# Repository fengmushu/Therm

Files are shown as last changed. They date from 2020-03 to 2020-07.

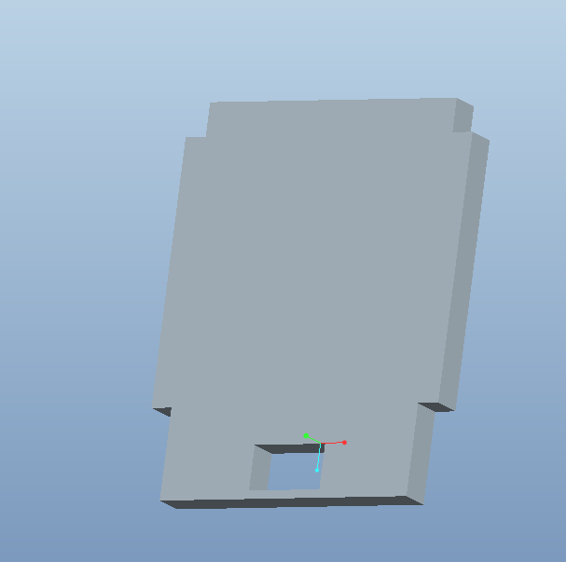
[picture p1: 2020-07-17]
doc/wm-smallgun/导光板设计资料/示意图.png

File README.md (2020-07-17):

[ROM]
- PB8-i2c-CLK
- PB9-i2c-DAT
- 可能是用于保存传感器NTC查表的
- 合法数据才会有i2c访问记录

[SPK]
- PD7-蜂鸣器

[LCD]
- LCD[1-4] - COM0/1/2/3 - PA9/10/11/12
- LCD[5-15] - S19/18/17/16/15/14/13/12/11/10/9 - PA4/5/6/7 - PC4/5 - PB0/1/2/10/11
- LCD[16-24] - S8/7/6/5/4/3/2/1/0 - PB12/13/14/15 - PC6/7/8/9 - PA8

[P1-DEBUG]
- SW-CLK
- SW-DIO
- VCC
- GND
- RSTB

[KEY]
- KEY[1:Trigger - 5] - PD6 - PC10/11/12 - PD2

[Anlog]
- PA15 - AV+ 3V
       - AV- -> GND
- PA0 -> 1-1.2v ViR
- PA1 -> NTC+800mV
- PA2 -> NTC-2000mV

- VIN+ 960mV
- VIN- 1000mV
- Yellow-NTC--2.0V
- Green-VIN--1000mV
- Black-NTC+-800mV
- Red-VIN+-960mV

[LED]
- LED-Light - PC13

Vra = Vcc - VntcL

- ('Vi(Tt)', array([-2.420154e+06,  5.435100e+04,  4.950000e+02]))
- ('Vi(Te)', array([ 1.589544e+06, -5.435100e+04, -4.950000e+02]))
- ('Ra(Te)', array([ 2.84148615e+05, -9.89025670e+03,  1.02357699e+02]))

- ViTt = At + Bt * Tt + Ct * Tt^2;
- ViTe = Ae + Be * te + Ce * te^2;

- 29-/+0.5 步长0.1
- fAPM, fCaBase, fHumFix;

#### MUST READ !!!
1. 标定部分, 需要预留Flash最后2个Block
2. 

原理:  
1. 传感器里面有两个单元: 光敏电池(辐射热堆) 和 温敏电阻(测环境温度); 
2. 光敏电池的电压 Vir 与 辐射源的温度 Tt 存在一张离散数据表 Vir-Tt;
3. 温敏电阻阻值 Ra 与 环境温度 Te 存在一张离散的数据表 Ra-Te;
4. 校准先后分为两步:
1. 标准温度下, 标定黑体
              * 操作: 黑体和环境都是35°和42°的稳定环境下, 测出对应的标定温度: 如 35.3, 41.8 分别保存到设备里面H,L
       2. 恒定黑体下, 标定环温
              * 操作: 改变环境温度, 测出相对于固定黑体温度的值, 计算NTC-变温校准系数

#### 历史数据存储
1. 物体模式和人体模式, 各自分别保存32组数据;
2. 显示时: 根据当前所选模式, 各自读取 1) 保存的历史数据, 直接显示;
3. 历史数据存储位置为: I2C ROM的前半部分;
4. 历史数据存取方式,用环形栈结构;
5. 物/人切换后, 历史数据下标复位到栈顶;

#### 校准数据保存
1. Flash 的 0xFC00 块存放产测和校准数据(最大块容量 512Byte);
2. I2C ROM 除了保存历史数据之外, 最后64Byte也保存一份校准数据;
3. Flash的校准数据与I2C的, 写入时保持同步;
4. Flash的校准数据与I2C的, 加载时只判断有无;
5. Flash的校准数据和I2C有差异时: 以I2C保存的为准(处理传感器差异, 不需要升级软件, 修改I2C即可);
6. 校准数据需要MagicNumber区别, 防止软件版本变更数据结构;

7. 校准数据里面需要包含传感器的拟合参数 --- 有待商榷;

Rx * 100K / (Rx+100K) * I + 100K * I = 2.5

Vx = Rx * 100K / (Rx + 100K) * I

I = (2.5 - Vx) / 100K

Vx = Rx * ( 2.5 - Vx) / ( Rx + 100K )

Vx * Rx + Vx * 100K = (2.5 - Vx) * Rx

Vx * 100K = (2.5 - 2 * Vx) * Rx

Rx = Vx * 100K /  (2.5 - 2 * Vx)

1. R45 2k
2. R41,R43,R46 1k
3. R44 680k

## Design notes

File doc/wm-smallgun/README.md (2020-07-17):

1. 第一排3颗按键,柄过长, 会导致装配之后按不下去, 或者螺丝打紧之后, 按不下去;
2. 电池仓, 尾部弹片会掉出去;
3. 屏幕底部 外框厚度差0.2mm, 导致屏幕装配不可靠;

4. 屏幕导电PIN脚间距: 0.5625mm, 屏幕和外壳框之间的缝隙 就有 0.68mm
5. RC复位电路设计优化

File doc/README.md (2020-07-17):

### 2020-05-05

1. 校准时, 允许一个点 37/42, 采样失败时, 继续重新采样;
2. 校准时, 至少采样3次, 间隔一个打印周期(50ms-100ms), 计算多次采样值, 方差为零才算有效值, 否则继续采样;
3. 超过 10 次都是无效值(说明手抖), 蜂鸣器长鸣告警, 重新进入校准;
4.

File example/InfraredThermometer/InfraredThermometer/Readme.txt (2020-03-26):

================================================================================
                                样例使用说明
================================================================================
版本历史 
日期        版本    负责人         IAR     MDK         描述
2020-03-12  SE2.0     Lux          xxx     5.26       first version
================================================================================
功能描述
================================================================================
本额温枪样例为开发过程版本，旨在提供基本功能模块单元的操作及架构，为应用开发者提供快速原型构建，
将更多的精力用在业务开发上及系统调试上。

================================================================================
测试环境
================================================================================
辅助工具:
---------------------

配套硬件参考:
---------------------
“Hm-Meter-源文件.rar”及“Hm-Meter-PDF BOM.rar”
硬件参考资料可向销售窗口获取

================================================================================
操作步骤
================================================================================
1) 程序编译后下载到配套方案板；
2) 复位或初次上电LCD全显闪烁两次，保持全显；
3) 参考软件流程（操作）进行验证；

================================================================================
功能说明
================================================================================
1）打开工程编译并运行。
2）可根据不同的具体硬件IO功能修改"board_stkhc32l13x.h"板级接口文件，或自行定义功能。
3）数据采集部分使用内部ADC连续16次采样取均值的方式采样外部经过OPA调理过的信号。
4) 显示部分提供了配套原理图“Hm-Meter-源文件.rar”及“Hm-Meter-PDF BOM.rar” 所使用LCD的数据结构及操作，同时包括HC32L13X_STK的LCD参考。
5) 数据处理算法参考“nna.h"及样例。
6) 按键及其他基础功能模块较为简单，通常为基本的IO操作，本应用提供了基本的初始化操作。

================================================================================
注意
================================================================================
-->>本样例实现了额温枪方案的基本方法及架构，基于华大MCU HC32L136进行构建，算法已基于现有硬件配套传感器进行验证；
-->>仅可为应用开发者提供快速原型参考，具体的端口、业务功能、数据处理应以实际采纳的硬件为准，进行程序修改及调试；
-->>如果硬件发生更改，请对应修改软件及配置;
-->>如果传感器发生更改，请更新“inf_config”中的V-T表及NTC表;
-->>LCD使用如有不同，需要根据手册修改编码及端口配置;
-->>本应用示例对于硬件及软件逻辑功能不做任何限制，主要用于参考原型，便于对进行自己产品的差异化开发;
================================================================================

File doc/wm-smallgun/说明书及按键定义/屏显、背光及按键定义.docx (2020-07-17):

# 屏显及按键

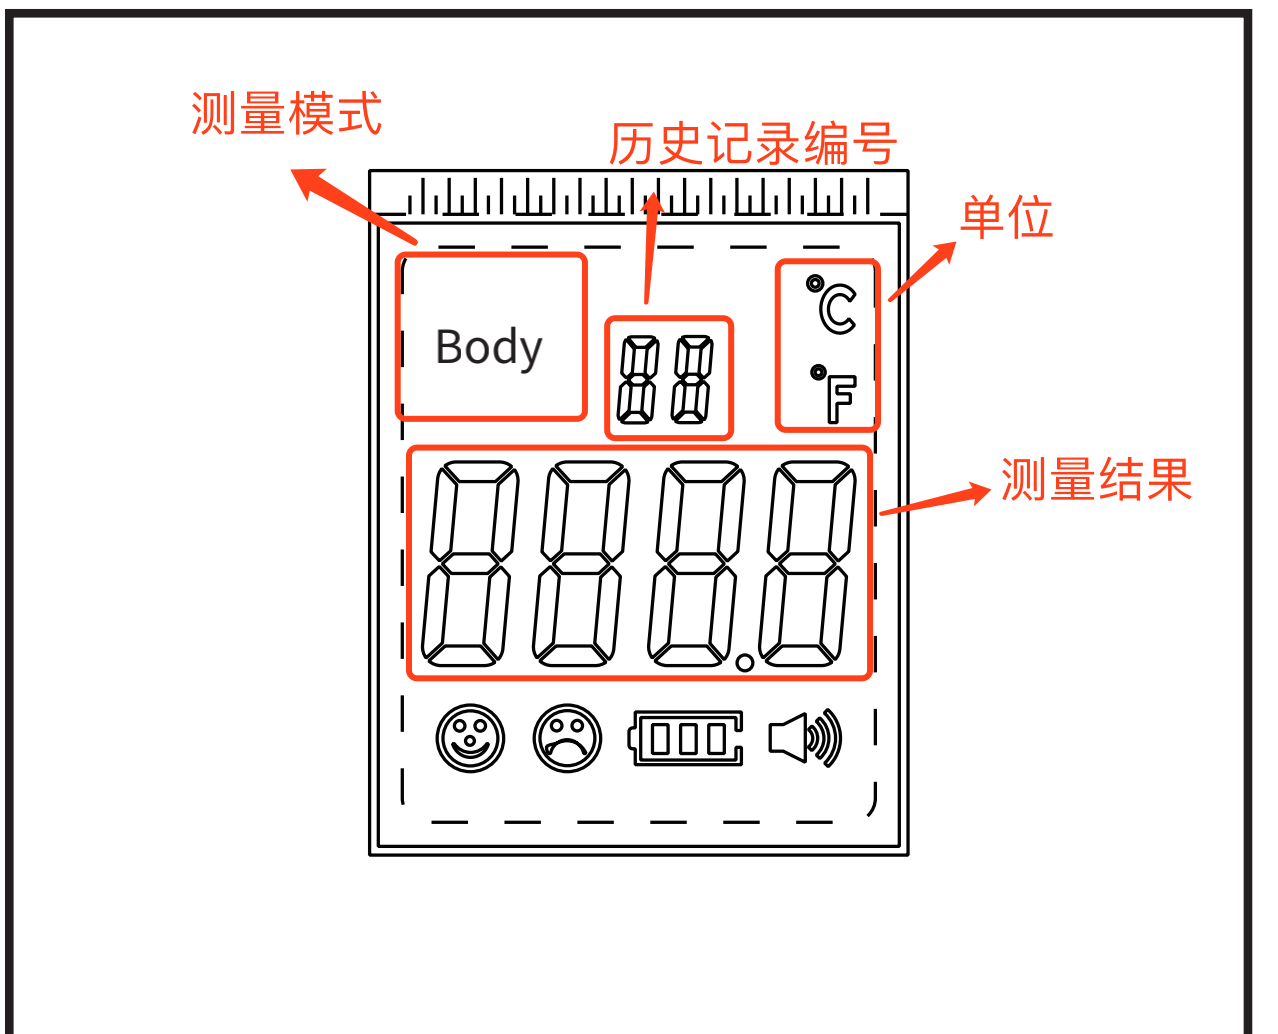
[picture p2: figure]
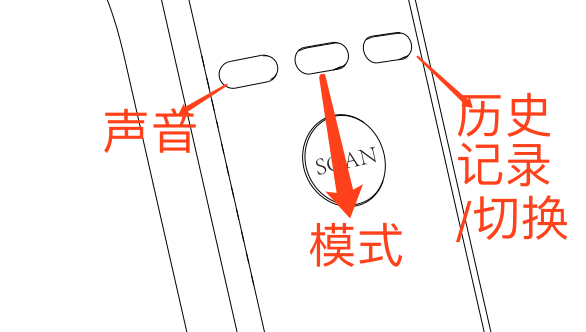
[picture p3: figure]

# 按键

## 声音

直接开启或关闭声音，影响屏幕上面的是否显示。

## 模式

两种设置

A：测试模式：物温模式或体温模式

B：单位模式：F or C

可以多次按此键进行设置切换

在A, B任一设置模式下，通过右侧切换键进行设置。

## 历史记录/切换

A. 在设置模式下，切换设置
B. 在扫描模式下进行，查看历史记录。

## 笑脸及背光

体温模式下：

=0 背光黄色，显示Lo，哭脸

< =37.2 背光绿色，笑脸

<=38 背光黄色，哭脸

其他 背光红色，哭脸

=100 背光红色，显示Hi，哭脸

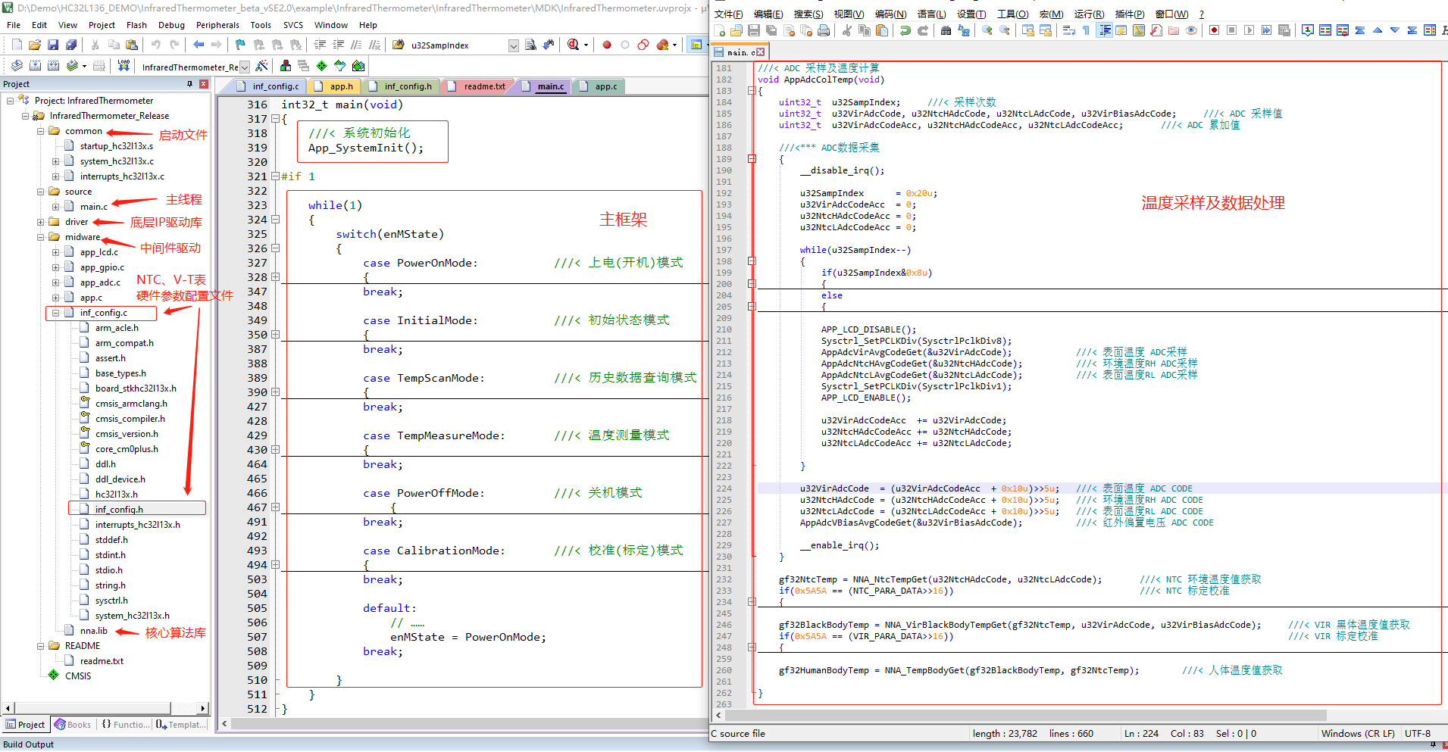
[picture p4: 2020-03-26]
工程及软件简介.png

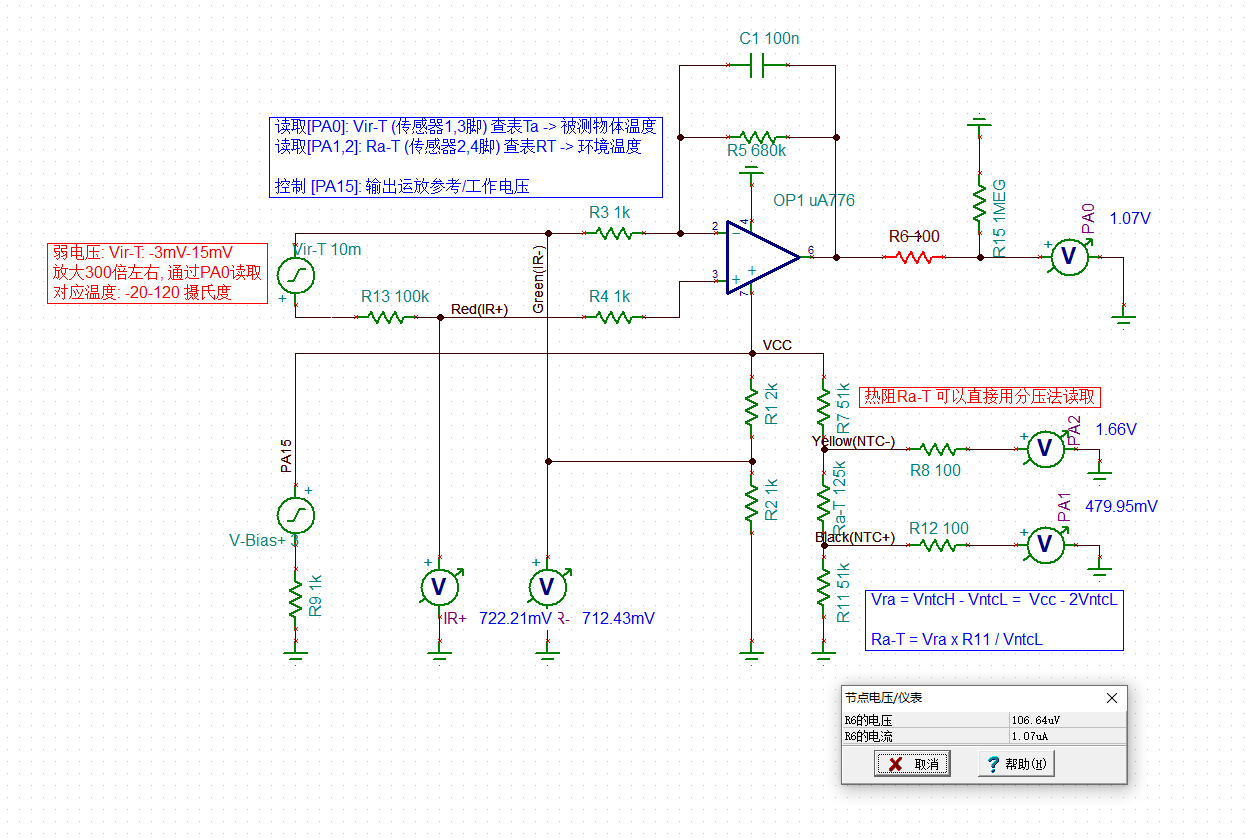
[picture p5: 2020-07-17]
TINA-SIM.png

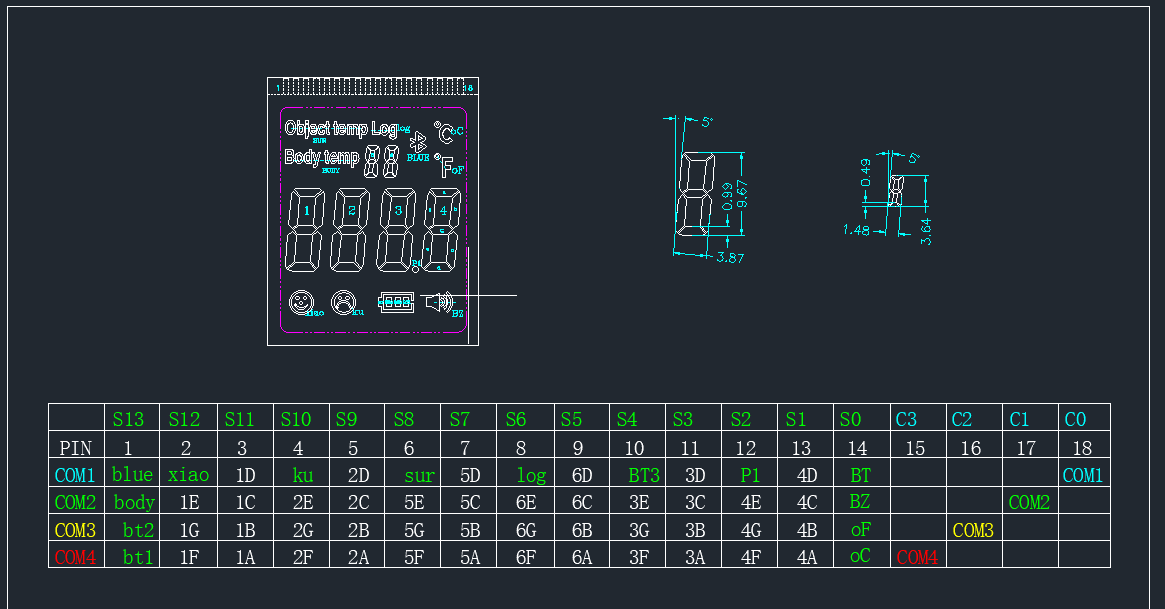
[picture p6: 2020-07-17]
doc/wm-smallgun/LCD-Define.png

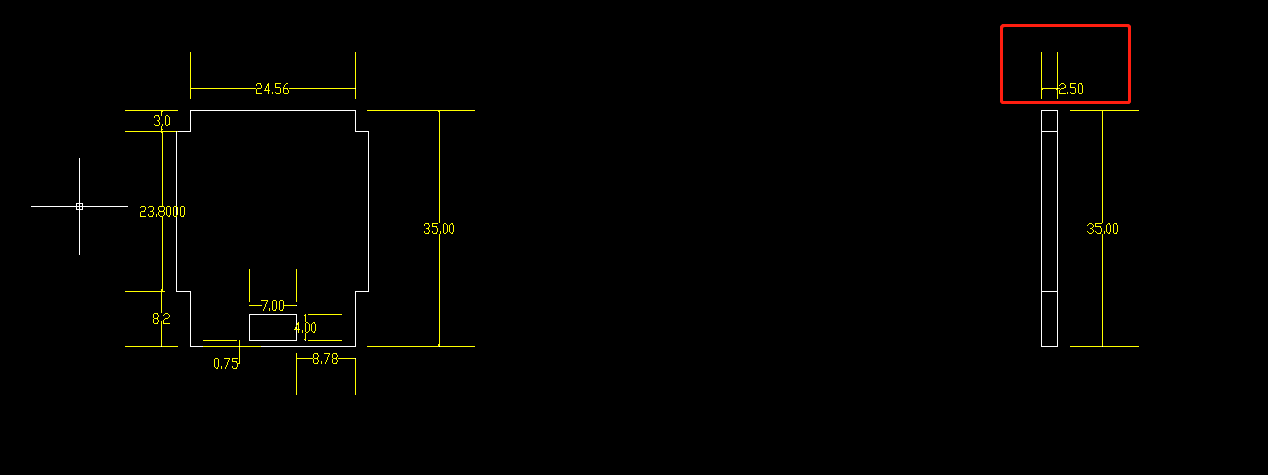
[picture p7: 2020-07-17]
doc/wm-smallgun/导光板设计资料/规格-不带贴纸.png

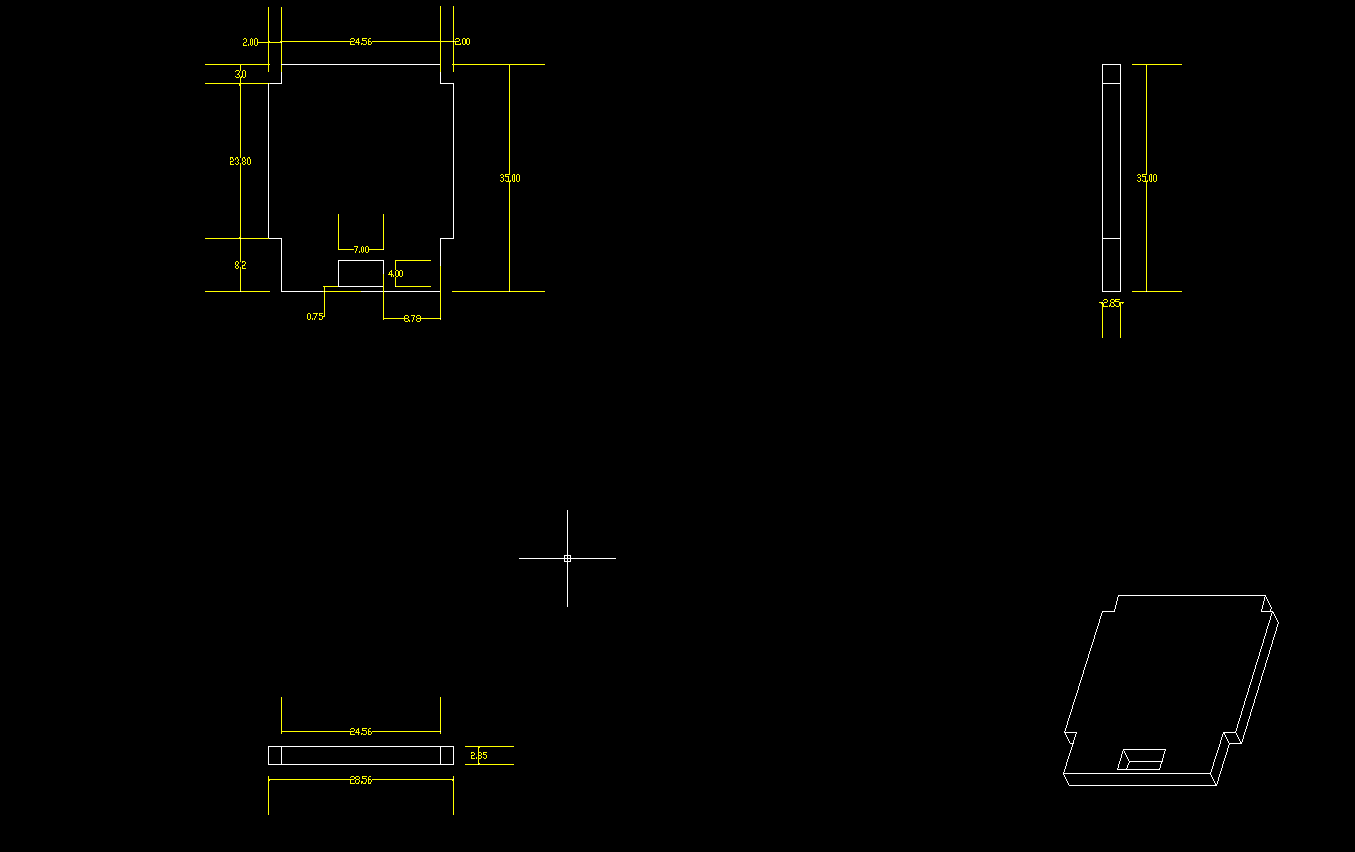
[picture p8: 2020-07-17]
doc/wm-smallgun/导光板设计资料/规则-带贴纸.png

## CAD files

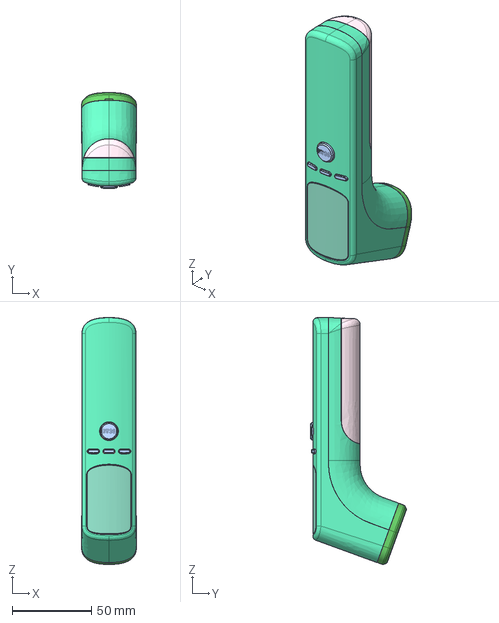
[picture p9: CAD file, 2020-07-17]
doc/wm-smallgun/小额温枪更新_asm-20200415.stp
34.8 x 60.6 x 156.1 mm

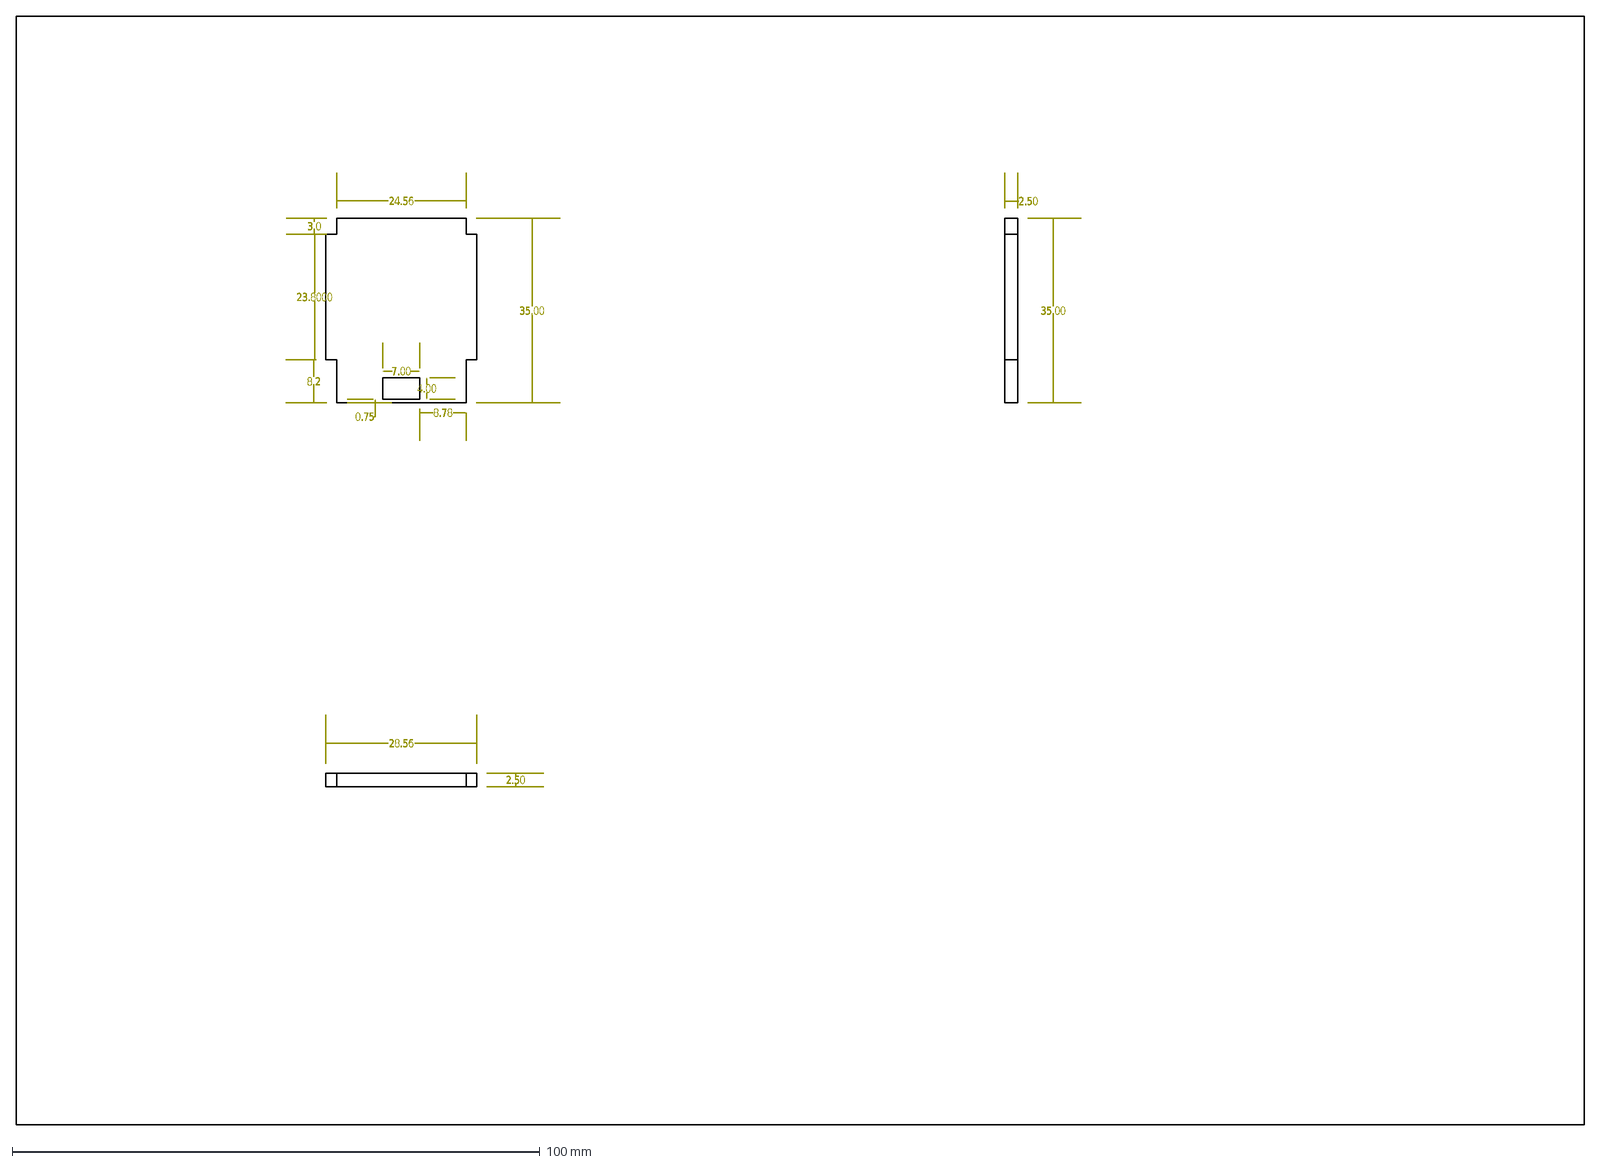
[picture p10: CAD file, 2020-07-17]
doc/wm-smallgun/导光板设计资料/pingmu2d.dxf
24.56
3.0
23.8000
8.2
35.00
0.75
7.00
4.00
8.78
2.50
28.56

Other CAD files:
doc/wm-smallgun/导光板设计资料/pingmu.dxf
doc/wm-smallgun/HCS50626小屏英文.dwg

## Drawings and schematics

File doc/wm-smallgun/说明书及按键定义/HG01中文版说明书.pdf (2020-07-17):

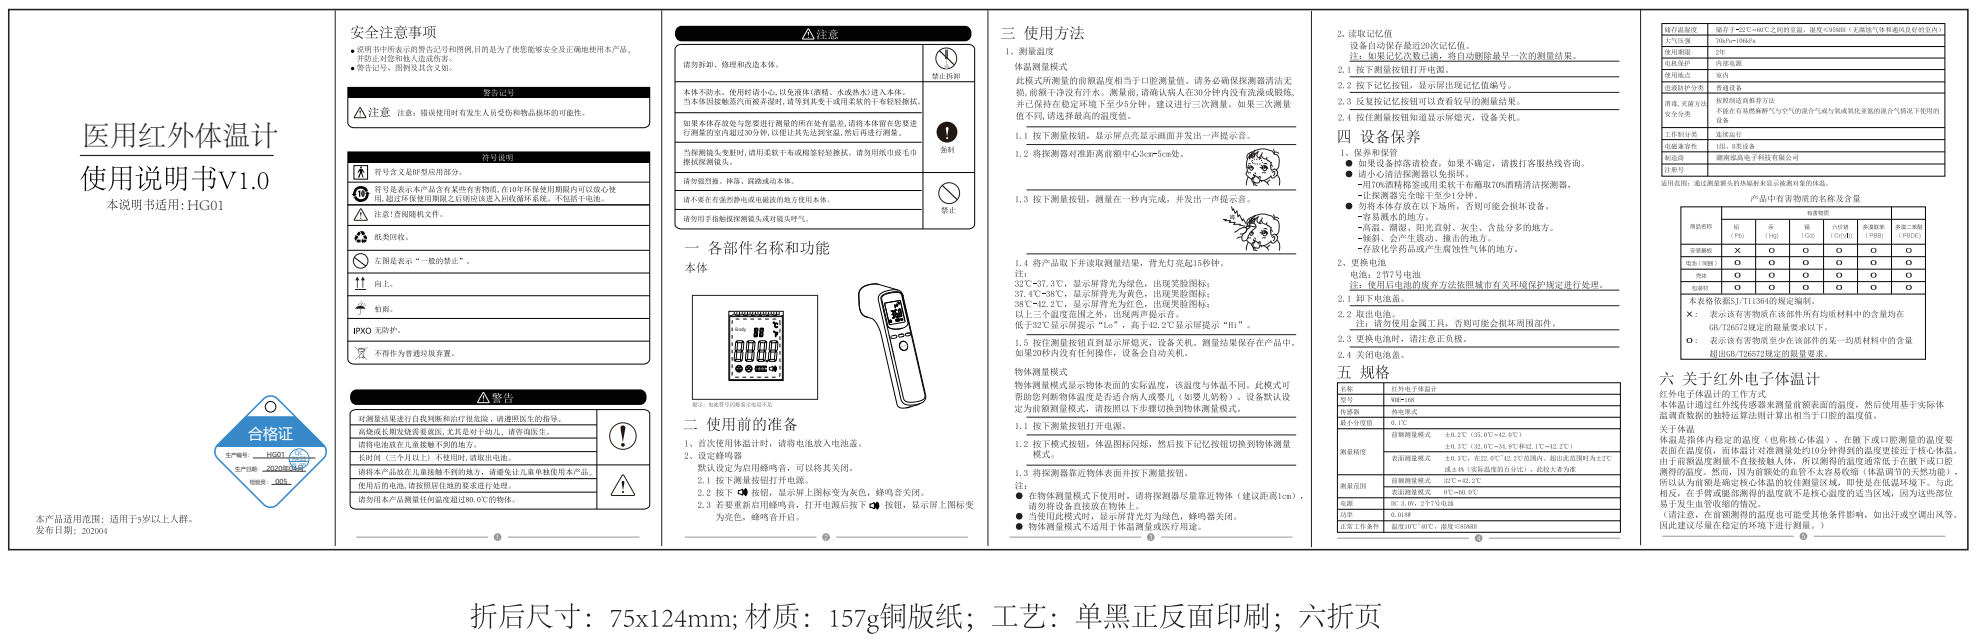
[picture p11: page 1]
医用红外体温计; 湖南泓高电子科技有限公司; Body; 合格证; 生产编号：; 生产日期： 2020年04月; 检验员： 005; QC PASS 检：005

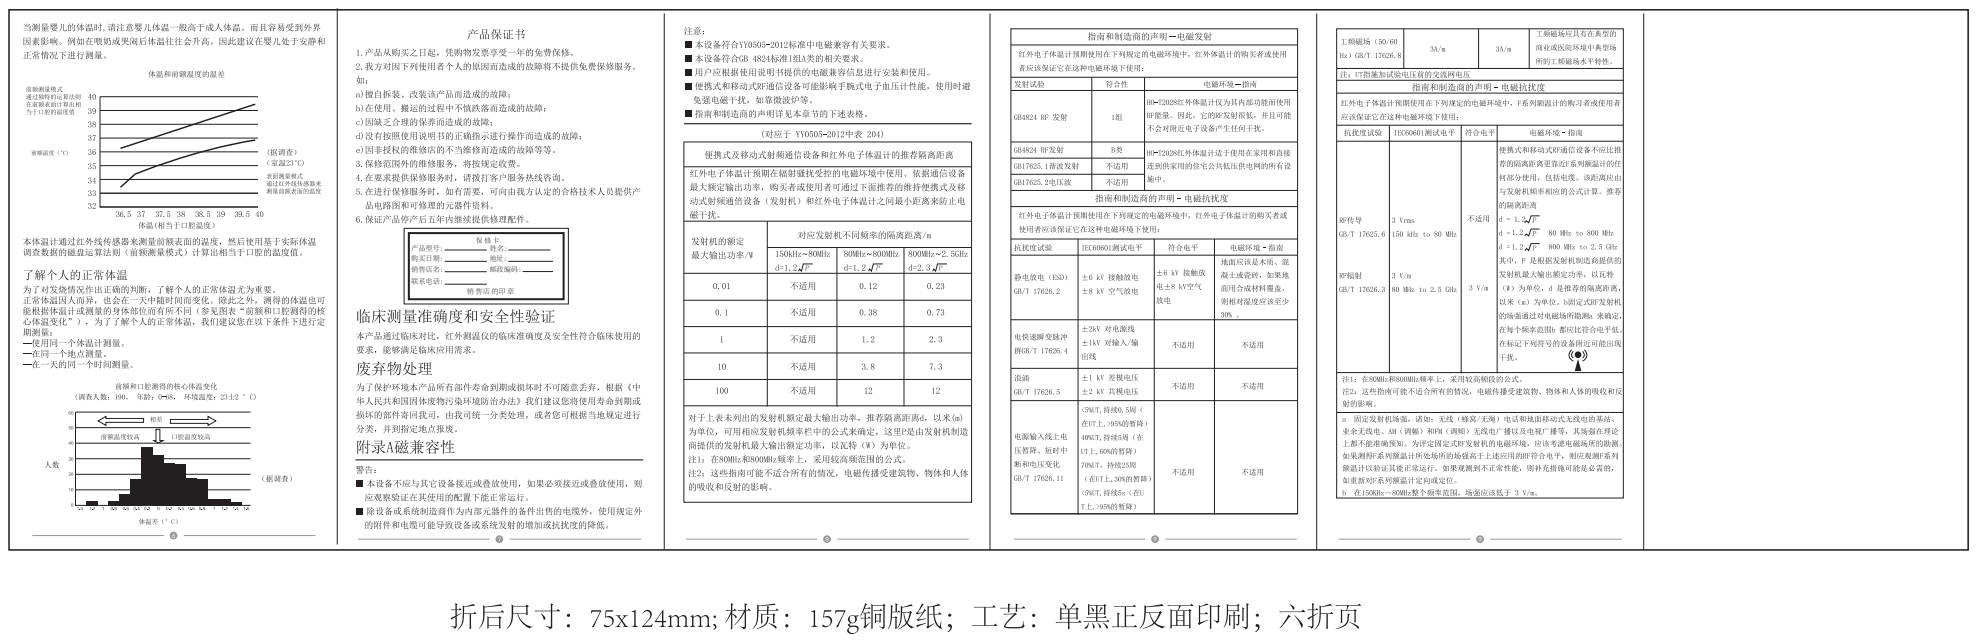
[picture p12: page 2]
产品型号： 购买日期： 销售店名： 联系电话：; 地址： 邮政编码：

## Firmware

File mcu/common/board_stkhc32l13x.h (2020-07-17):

/******************************************************************************
* Copyright (C) 2017, Huada Semiconductor Co.,Ltd All rights reserved.    
*
* This software is owned and published by: 
* Huada Semiconductor Co.,Ltd ("HDSC").
*
* BY DOWNLOADING, INSTALLING OR USING THIS SOFTWARE, YOU AGREE TO BE BOUND 
* BY ALL THE TERMS AND CONDITIONS OF THIS AGREEMENT.
*
* This software contains source code for use with HDSC 
* components. This software is licensed by HDSC to be adapted only 
* for use in systems utilizing HDSC components. HDSC shall not be 
* responsible for misuse or illegal use of this software for devices not 
* supported herein. HDSC is providing this software "AS IS" and will 
* not be responsible for issues arising from incorrect user implementation 
* of the software.  
*
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
* This software may be replicated in part or whole for the licensed use, 
* with the restriction that this Disclaimer and Copyright notice must be 
* included with each copy of this software, whether used in part or whole, 
* at all times.
*/
/******************************************************************************/
/** \file stkhc32l13x.h
 **
 ** stk board common define.
 ** @link SampleGroup Some description @endlink
 **
 **   - 2018-03-09  1.0  Lux First version.
 **
 ******************************************************************************/
#ifndef __BOARD_STKHC32L13X_H__
#define __BOARD_STKHC32L13X_H__

///< XTH
#define SYSTEM_XTH          (32*1000*1000u)     ///< 32MHz

///< XTL
#define SYSTEM_XTL          (32768u)            ///< 32768Hz

///< M GPIO KEYS
#define M_KEY_LEFT_PORT       GpioPortC
#define M_KEY_LEFT_PIN        GpioPin10
#define M_KEY_MID_PORT       GpioPortC
#define M_KEY_MID_PIN        GpioPin11
#define M_KEY_RIGHT_PORT       GpioPortC
#define M_KEY_RIGHT_PIN        GpioPin12
#define M_KEY_TRIG_PORT       GpioPortD
#define M_KEY_TRIG_PIN        GpioPin6
#define M_KEY_SWITCH_PORT       GpioPortD
#define M_KEY_SWITCH_PIN        GpioPin2

///< M ADC EXREF
// #define M_ADC_EXREF_PORT  GpioPortB
// #define M_ADC_EXREF_PIN   GpioPin1

///< M ADC CHx
// V-OUT
#define M_ADC_VOUT_PORT    GpioPortA
#define M_ADC_VOUT_PIN     GpioPin0
// NTC+
#define M_ADC_NTCH_PORT  GpioPortA
#define M_ADC_NTCH_PIN   GpioPin1
// NTC-
#define M_ADC_NTCL_PORT  GpioPortA
#define M_ADC_NTCL_PIN   GpioPin2
// VIN +/- --- V2.0硬件, 已删除
// V-Bias-REF-IN
// #define M_ADC_VREF_PORT  GpioPortA
// #define M_ADC_VREF_PIN   GpioPin3
// V-Bias-ON/OFF
#define M_ADC_VBIRS_PORT  GpioPortA
#define M_ADC_VBIRS_PIN   GpioPin15
// USE PB07 as ADC_VOUT_CTRL_PIN
#define M_ADC_VBIRS_EN_PORT     GpioPortB
#define M_ADC_VBIRS_EN_PIN      GpioPin7

///< M LCD SEG/COM
#define M_LCD_COM0_PORT   GpioPortA
#define M_LCD_COM0_PIN    GpioPin9
#define M_LCD_COM1_PORT   GpioPortA
#define M_LCD_COM1_PIN    GpioPin10
#define M_LCD_COM2_PORT   GpioPortA
#define M_LCD_COM2_PIN    GpioPin11
#define M_LCD_COM3_PORT   GpioPortA
#define M_LCD_COM3_PIN    GpioPin12
//< M LCD SEG0-19
#define M_LCD_SEG0_PORT   GpioPortA
#define M_LCD_SEG0_PIN    GpioPin8 
#define M_LCD_SEG1_PORT   GpioPortC
#define M_LCD_SEG1_PIN    GpioPin9 
#define M_LCD_SEG2_PORT   GpioPortC
#define M_LCD_SEG2_PIN    GpioPin8 
#define M_LCD_SEG3_PORT   GpioPortC
#define M_LCD_SEG3_PIN    GpioPin7 
#define M_LCD_SEG4_PORT   GpioPortC
#define M_LCD_SEG4_PIN    GpioPin6 
#define M_LCD_SEG5_PORT   GpioPortB
#define M_LCD_SEG5_PIN    GpioPin15
#define M_LCD_SEG6_PORT   GpioPortB
#define M_LCD_SEG6_PIN    GpioPin14
#define M_LCD_SEG7_PORT   GpioPortB
#define M_LCD_SEG7_PIN    GpioPin13
#define M_LCD_SEG8_PORT   GpioPortB
#define M_LCD_SEG8_PIN    GpioPin12
#define M_LCD_SEG9_PORT   GpioPortB
#define M_LCD_SEG9_PIN    GpioPin11
#define M_LCD_SEG10_PORT   GpioPortB
#define M_LCD_SEG10_PIN    GpioPin10
#define M_LCD_SEG11_PORT   GpioPortB
#define M_LCD_SEG11_PIN    GpioPin2
#define M_LCD_SEG12_PORT   GpioPortB
#define M_LCD_SEG12_PIN    GpioPin1
#define M_LCD_SEG13_PORT   GpioPortB
#define M_LCD_SEG13_PIN    GpioPin0
#define M_LCD_SEG14_PORT   GpioPortC
#define M_LCD_SEG14_PIN    GpioPin5
#define M_LCD_SEG15_PORT   GpioPortC
#define M_LCD_SEG15_PIN    GpioPin4
#define M_LCD_SEG16_PORT   GpioPortA
#define M_LCD_SEG16_PIN    GpioPin7
#define M_LCD_SEG17_PORT   GpioPortA
#define M_LCD_SEG17_PIN    GpioPin6
#define M_LCD_SEG18_PORT   GpioPortA
#define M_LCD_SEG18_PIN    GpioPin5
#define M_LCD_SEG19_PORT   GpioPortA
#define M_LCD_SEG19_PIN    GpioPin4

//< M BEEP
#define M_BEEP_PORT       GpioPortD
#define M_BEEP_PIN        GpioPin7

///< M LED
#define M_LED_RED_PORT       GpioPortC
#define M_LED_RED_PIN        GpioPin14
#define M_LED_GREEN_PORT       GpioPortC
#define M_LED_GREEN_PIN        GpioPin13

///< M I2C EEPROM
#define M_E2_I2C0_SCL_PORT       GpioPortB
#define M_E2_I2C0_SCL_PIN        GpioPin8
#define M_E2_I2C0_SDA_PORT       GpioPortB
#define M_E2_I2C0_SDA_PIN        GpioPin9

// DBG_CONSOLE
#define DBG_CONSOLE         M0P_UART1
#define DBG_CONSOLE_GPIO    GpioPortD
#define DBG_CONSOLE_TX      GpioPin0
#define DBG_CONSOLE_RX      GpioPin1

#endif

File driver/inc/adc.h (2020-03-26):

/******************************************************************************
* Copyright (C) 2017, Huada Semiconductor Co.,Ltd All rights reserved.
*
* This software is owned and published by:
* Huada Semiconductor Co.,Ltd ("HDSC").
*
* BY DOWNLOADING, INSTALLING OR USING THIS SOFTWARE, YOU AGREE TO BE BOUND
* BY ALL THE TERMS AND CONDITIONS OF THIS AGREEMENT.
*
* This software contains source code for use with HDSC
* components. This software is licensed by HDSC to be adapted only
* for use in systems utilizing HDSC components. HDSC shall not be
* responsible for misuse or illegal use of this software for devices not
* supported herein. HDSC is providing this software "AS IS" and will
* not be responsible for issues arising from incorrect user implementation
* of the software.
*
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
* This software may be replicated in part or whole for the licensed use,
* with the restriction that this Disclaimer and Copyright notice must be
* included with each copy of this software, whether used in part or whole,
* at all times.
*/
/******************************************************************************/
/** \file adc.h
 **
 ** Header file for AD Converter functions
 ** @link ADC Group Some description @endlink
 **
 **   - 2017-06-28 Alex    First Version
 **
 ******************************************************************************/

#ifndef __ADC_H__
#define __ADC_H__


/******************************************************************************/
/* Include files                                                              */
/******************************************************************************/
#include "ddl.h"


/* C binding of definitions if building with C++ compiler */
#ifdef __cplusplus
extern "C"
{
#endif

/**
 ******************************************************************************
 ** \defgroup AdcGroup AD Converter (ADC)
  **
 ******************************************************************************/
 
//@{

/******************************************************************************
 * Global definitions
 ******************************************************************************/
#define ADC_SCAN_CH0_EN     (0x1u)           /*!< SCAN模式使用ADC CH0 */
#define ADC_SCAN_CH1_EN     (0x1u<<1)        /*!< SCAN模式使用ADC CH1 */
#define ADC_SCAN_CH2_EN     (0x1u<<2)        /*!< SCAN模式使用ADC CH2 */
#define ADC_SCAN_CH3_EN     (0x1u<<3)        /*!< SCAN模式使用ADC CH3 */
#define ADC_SCAN_CH4_EN     (0x1u<<4)        /*!< SCAN模式使用ADC CH4 */
#define ADC_SCAN_CH5_EN     (0x1u<<5)        /*!< SCAN模式使用ADC CH5 */
#define ADC_SCAN_CH6_EN     (0x1u<<6)        /*!< SCAN模式使用ADC CH6 */
#define ADC_SCAN_CH7_EN     (0x1u<<7)        /*!< SCAN模式使用ADC CH7 */


/******************************************************************************
 ** Global type definitions
 *****************************************************************************/

 /**
 ******************************************************************************
 ** \brief ADC转换模式
 *****************************************************************************/
typedef enum en_adc_mode
{
    AdcSglMode  = 0u,           /*!< 单输入通道单次转换模式 */
    AdcScanMode = 1u,           /*!< 多输入通道顺序/插队扫描转换模式*/   
}en_adc_mode_t;

/**
 ******************************************************************************
 ** \brief ADC时钟分频选择
 *****************************************************************************/
typedef enum en_adc_clk_sel
{
    AdcMskClkDiv1  = 0u<<2,        /*!< PCLK */
    AdcMskClkDiv2  = 1u<<2,        /*!< 1/2 PCLK */
    AdcMskClkDiv4  = 2u<<2,        /*!< 1/4 PCLK */
    AdcMskClkDiv8  = 3u<<2,        /*!< 1/8 PCLK */
} en_adc_clk_div_t;

/**
 ******************************************************************************
 ** \brief ADC参考电压
 *****************************************************************************/
typedef enum en_adc_ref_vol_sel
{
    AdcMskRefVolSelInBgr1p5 = 0u<<9,        /*!<内部参考电压1.5V(SPS<=200kHz)*/
    AdcMskRefVolSelInBgr2p5 = 1u<<9,        /*!<内部参考电压2.5V(avdd>3V,SPS<=200kHz)*/
    AdcMskRefVolSelExtern1  = 2u<<9,        /*!<外部输入(max avdd)   PB01*/
    AdcMskRefVolSelAVDD     = 3u<<9,        /*!<AVDD*/
}en_adc_ref_vol_sel_t;

/**
 ******************************************************************************
 ** \brief ADC转换通道选择
 *****************************************************************************/
typedef enum en_adc_samp_ch_sel
{
    AdcExInputCH0    =  0u,        /*!<使用PA00*/
    AdcExInputCH1    =  1u,        /*!<使用PA01*/
    AdcExInputCH2    =  2u,        /*!<使用PA02*/
    AdcExInputCH3    =  3u,        /*!<使用PA03*/
    AdcExInputCH4    =  4u,        /*!<使用PA04*/
    AdcExInputCH5    =  5u,        /*!<使用PA05*/
    AdcExInputCH6    =  6u,        /*!<使用PA06*/
    AdcExInputCH7    =  7u,        /*!<使用PA07*/
    AdcExInputCH8    =  8u,        /*!<使用PB00*/
    AdcExInputCH9    =  9u,        /*!<使用PB01*/
    AdcExInputCH10   =  10u,       /*!<使用PC00*/
    AdcExInputCH11   =  11u,       /*!<使用PC01*/
    AdcExInputCH12   =  12u,       /*!<使用PC02*/
    AdcExInputCH13   =  13u,       /*!<使用PC03*/
    AdcExInputCH14   =  14u,       /*!<使用PC04*/
    AdcExInputCH15   =  15u,       /*!<使用PC05*/
    AdcExInputCH16   =  16u,       /*!<使用PB02*/
    AdcExInputCH17   =  17u,       /*!<使用PB10*/
    AdcExInputCH18   =  18u,       /*!<使用PB11*/
    AdcExInputCH19   =  19u,       /*!<使用PB12*/
    AdcExInputCH20   =  20u,       /*!<使用PB13*/
    AdcExInputCH21   =  21u,       /*!<使用PB14*/
    AdcExInputCH22   =  22u,       /*!<使用PB15*/
    AdcExInputCH23   =  23u,       /*!<使用PE15*/
    AdcOPA0Input     =  24u,       /*!<使用通道8输入OPA0*/
    AdcOPA1Input     =  25u,       /*!<使用通道8输入OPA1*/

    AdcOPA2Input     =  26u,       /*!<使用通道8输入OPA2*/                     
    AdcAVccdiv3Input =  27u,       /*!<使用1/3 AVCC(必须使用输入增益)*/
    AdcAiTsInput     =  28u,       /*!<使用内置温度传感器BGR_TS(必须使用输入增益)*/
    AdcVref1_2Input  =  29u,       /*!<使用内部基准1.2V(必须使用输入增益)*/

}en_adc_samp_ch_sel_t;

 /**
 ******************************************************************************
 ** \brief ADC输入信号放大器控制
 *****************************************************************************/
typedef enum en_adc_op_buf
{
    AdcMskBufEnable  = 1u<<11,          /*!< 打开放大器BUF */
    AdcMskBufDisable = 0u,              /*!< 关闭放大器BUF */  
} en_adc_op_buf_t;

/**
 ******************************************************************************
 ** \brief ADC采样周期选择
 *****************************************************************************/
typedef enum en_adc_samp_cycle_sel
{
    AdcMskSampCycle4Clk  =  0u<<12,        /*!<4个采样时钟*/
    AdcMskSampCycle6Clk  =  1u<<12,        /*!<6个采样时钟*/
    AdcMskSampCycle8Clk  =  2u<<12,        /*!<8个采样时钟*/
    AdcMskSampCycle12Clk =  3u<<12,        /*!<12个采样时钟*/

}en_adc_samp_cycle_sel_t;

/**
 ******************************************************************************
 ** \brief ADC内部参考电压使能控制
 *****************************************************************************/
typedef enum en_adc_in_ref
{
    AdcMskInRefEnable  = 1u<<14,          /*!< 内部参考电压使能 */
    AdcMskInRefDisable = 0u,              /*!< 内部参考电压关闭 */  
}en_adc_in_ref_t;

/**
 ******************************************************************************
 ** \brief ADC周边模块反射源选择
 *****************************************************************************/
typedef enum en_adc_trig_sel
{
    AdcMskTrigTimer0     =  1u<<0,         /*!<选择timer0中断源，自动触发ADC采样*/
    AdcMskTrigTimer1     =  1u<<1,         /*!<选择timer1中断源，自动触发ADC采样*/
    AdcMskTrigTimer2     =  1u<<2,         /*!<选择timer2中断源，自动触发ADC采样*/
    AdcMskTrigTimer3     =  1u<<3,         /*!<选择timer3中断源，自动触发ADC采样*/
    AdcMskTrigTimer4     =  1u<<4,         /*!<选择timer4中断源，自动触发ADC采样*/
    AdcMskTrigTimer5     =  1u<<5,         /*!<选择timer5中断源，自动触发ADC采样*/
    AdcMskTrigTimer6     =  1u<<6,         /*!<选择timer6中断源，自动触发ADC采样*/
    AdcMskTrigUart0      =  1u<<7,         /*!<选择uart0中断源，自动触发ADC采样*/
    AdcMskTrigUart1      =  1u<<8,         /*!<选择uart1中断源，自动触发ADC采样*/
    AdcMskTrigLpuart0    =  1u<<9,         /*!<选择lpuart0中断源，自动触发ADC采样*/
    AdcMskTrigLpuart1    =  1u<<10,        /*!<选择lpuart1中断源，自动触发ADC采样*/
    AdcMskTrigVC0        =  1u<<11,        /*!<选择VC0中断源，自动触发ADC采样*/
    AdcMskTrigVC1        =  1u<<12,        /*!<选择VC1中断源，自动触发ADC采样*/
    AdcMskTrigRTC        =  1u<<13,        /*!<选择RTC中断源，自动触发ADC采样*/
    AdcMskTrigPCA        =  1u<<14,        /*!<选择PCA中断源，自动触发ADC采样*/
    AdcMskTrigSPI0       =  1u<<15,        /*!<选择SPI0中断源，自动触发ADC采样*/
    AdcMskTrigSPI1       =  1u<<16,        /*!<选择SPI1中断源，自动触发ADC采样*/
    AdcMskTrigDMA        =  1u<<17,        /*!<选择DMA中断源，自动触发ADC采样*/
    AdcMskTrigPA03       =  1u<<18,        /*!<选择PA03中断源，自动触发ADC采样*/
    AdcMskTrigPB03       =  1u<<19,        /*!<选择PB03中断源，自动触发ADC采样*/
    AdcMskTrigPC03       =  1u<<20,        /*!<选择PC03中断源，自动触发ADC采样*/
    AdcMskTrigPD03       =  1u<<21,        /*!<选择PD03中断源，自动触发ADC采样*/
    AdcMskTrigPA07       =  1u<<22,        /*!<选择PA07中断源，自动触发ADC采样*/
    AdcMskTrigPB07       =  1u<<23,        /*!<选择PB07中断源，自动触发ADC采样*/
    AdcMskTrigPC07       =  1u<<24,        /*!<选择PC07中断源，自动触发ADC采样*/
    AdcMskTrigPD07       =  1u<<25,        /*!<选择PD07中断源，自动触发ADC采样*/
    AdcMskTrigPA11       =  1u<<26,        /*!<选择PA11中断源，自动触发ADC采样*/
    AdcMskTrigPB11       =  1u<<27,        /*!<选择PB11中断源，自动触发ADC采样*/
    AdcMskTrigPC11       =  1u<<28,        /*!<选择PC11中断源，自动触发ADC采样*/
    AdcMskTrigPA15       =  1u<<29,        /*!<选择PA15中断源，自动触发ADC采样*/
    AdcMskTrigPB15       =  1u<<30,        /*!<选择PB15中断源，自动触发ADC采样*/
    AdcMskTrigPC15       =  1u<<31,        /*!<选择PC15中断源，自动触发ADC采样*/
}en_adc_trig_sel_t;
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

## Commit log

2020-03-29 sensor read data ok
2020-03-31 环境温度 拟合采用完成
2020-03-31 拟合 Vir-T 曲线, 区间映射尚未开始调整
2020-04-01 查表和拟合 计算结果基本匹配
2020-04-06 calibration API finished
2020-04-06 GPIO for led added
2020-04-07 app_key: add note on key voltage level
2020-04-07 main: init i2c for calibration mode
2020-04-07 board_stkhc32l13x: revert gpio define for keys
2020-04-07 fsm: beep once on power on
2020-04-07 fsm: save data to i2c on power_off state
2020-04-07 change led set
2020-04-08 main: lvd irq to set battery low icon
2020-04-08 main: move rtc/pmu init after calibration mode
    do not put into sleep in calibration mode
2020-04-08 fsm: print scan result
2020-04-08 alert LED color supported
2020-04-09 tnna: support more sensors
2020-04-09 app_main: update led light logic
2020-04-09 Sample 4 times avarage
2020-04-09 fsm: move lcd show all to power on
    to accelerate sleep wake up
2020-04-09 sleep: turn off lcd to save power
2020-04-09 pwroff: change led color to orange
2020-04-10 app_main: body alarm: quick di-di-di-di-di
2020-04-10 add sensor MTS01
2020-04-11 engineer mode display AMP when cali, Env temp and sample when ADC
2020-04-11 change sensor type in cali mode supported
2020-04-11 release mts01
    print fAMP if error ocurrupted
    default load cali sensor index
2020-04-12 USE GPIO-PB07 as ADC power line
2020-04-13 fixup 2.5v internal ref vot
2020-04-13 add sensor b7f55
2020-04-13 remove unused sensors F55,B7
2020-04-21 add a doc of screen
    [HCS50626小屏英文.dwg]
2020-04-21 add doc of 导光
    [pingmu.dxf, pingmu2d.dxf]
2020-04-21 add shell doc
    [小额温枪更新_asm-20200415.stp]
2020-04-27 use absulote Voltage for ADC
2020-05-05 Enhanced calibration algorithm accuracy
2020-05-05 limit uRa to check if SENSOR is ok
2020-05-05 must more than 3 samples
2020-05-06 limit ViR to 0.7v-1.5v as 37-42
2020-05-14 Skin fixup to 34 degree, update Varience samples
2020-05-20 app_key: printf() in interrupt handler will corrupt memorygit add midware/src/app_key.c
2020-05-21 app_i2c: replace printf() by DBG_PRINT()
2020-05-21 app_cal: replace printf() with DBG_PRINT()
2020-05-22 app_cal: refine calibration display
    keep the behavior same as previous
2020-05-22 as cal 3->1 times sample
2020-05-25 fsm_core: hide debug printf by default
2020-06-19 33-degree power on
